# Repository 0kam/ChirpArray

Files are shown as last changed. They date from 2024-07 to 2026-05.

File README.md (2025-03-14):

# `ChirpArray`: a low-cost, easy-to-build microphone array for long-term ecoacoustic monitoring 

## Overview
`ChirpArray` is a microphone array for outdoor recording projects.  
It utilizes Sony's Spresense microcontroller as a processing module.
See https://doi.org/10.1111/2041-210X.14474 for more detail.

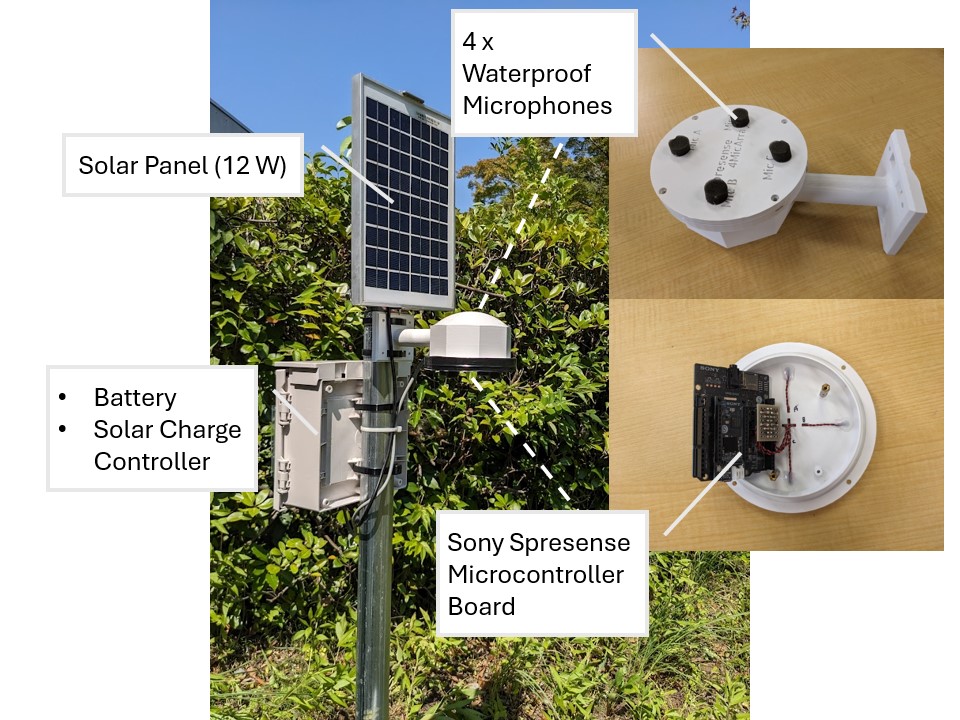
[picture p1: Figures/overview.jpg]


## Features
- **Up to 4ch recording:**  
    `ChirpArray` has 4 microphones to enable sound source localization.
- **Flexible recording setting and scheduling:**  
    Plenty of options for various research projects:
    * Sampling rate (16 kHz ~ 192 kHz)
    * Channels of recording (monaural, stereo, 4 channels)
    * Audio codec (WAV or MP3)
    * Recording schedule (see below) 
- **Low power consumption:**  
    `ChirpArray` can run with a 12 W solar power system due to Spresense's low power features.
- **Automated time correction using on-board GNSS**
- **Low cost:**  
    The whole system with solar power system costs about $200.
- **Easy to reproduce:**  
    All parts are available online.  
    No professional skills are required to assemble `ChirpArray`.

## Parts list
### `ChirpArray`  
| product name | product type | manufacture | price | quantity |
| --- | --- | --- | --- | --- |
| Spresense Main Board | Main processing board | SONY | ¥6000 | 1 |
| Spresense Extension Board | Extension board for microphone inputs | SONY | ¥4000 | 1 |
| CME-1538-100LB | Analogue microphone | CUI Devices | ¥500 | 4 |
| 2.2 kΩ carbon resister | general resister |  | Under ¥10 | 4 |
| Stripboard (36 mm x 24 mm) | general stripboard |  | Under ¥100 | 1 |
| pin header (2 x 8) | general pin header |  | Under ¥50 | 1 |
| micro SD Card (512GB) | general micro SD card |  | ¥10000 | 1 |

### *Optional:* Parts Example for Solar Powered Applications
| product name | product type | manufacture | price | quantity |
| --- | --- | --- | --- | --- |
| SY-M12W-12 | Solar Panel (12 W) | SANYOOO solar | ¥2500 | 1 |
| SA-BA10 | Solar Charge Controller | DENRYO | ¥4000 | 1 |
| WP7.2-12 | Battery (12 V, 7,2 Ah) | Kung Long Batteries Industrial | ¥3000 | 1 |

### *Optional* recommended off-the-shelf waterproof box
[Takachi BCAP151509G](https://www.takachi-el.co.jp/assets/attachments/images/BCAP151509G.pdf) (¥1,600)

## Hardware Assembling

### Water-proof enclosures
First, choose a case to house the Spresense. While we have published 3D models of cases that can be printed with a 3D printer, you can also use commercially available waterproof boxes for outdoor installations. If you opt for a commercially available case, select one with enough space to accommodate the Spresense Extension Board (at least 90mm x 90mm x 30mm). Commercially available cases tend to offer better waterproofing, so if you're installing the device near a pond or in a high-humidity environment, it might be better to go with a commercially available case.
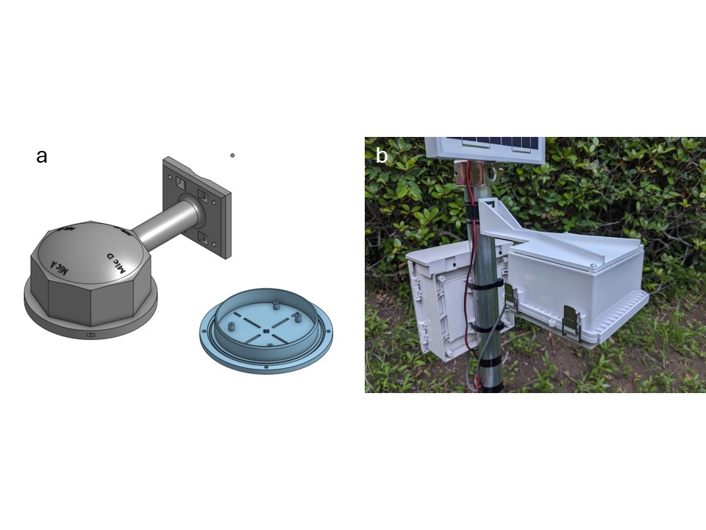
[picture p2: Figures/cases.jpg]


### Placing microphones
Next, arrange each microphone at equal intervals around the circumference of an 8cm diameter circle. If you are using a printable case, attach the microphones as shown in the picture below, and route the wires inside the case. Seal the wire entry points with adhesive. If you are using a commercially available case, drill holes in the case to attach the microphones directly. We also provide a 3D model for a microphone mounting plate, which you can print and use with any cases (in `3Dprintables/off_the_shelf_cases/MicrophoneAdaptor.stl`). To avoid rain damage, please install the microphones on the underside of the case.

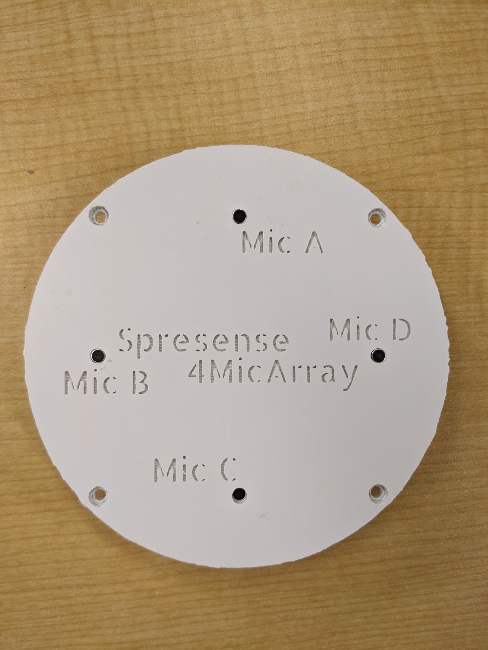
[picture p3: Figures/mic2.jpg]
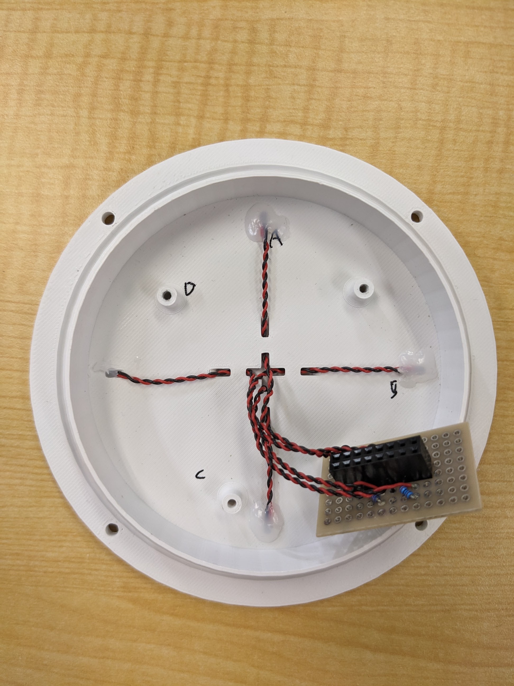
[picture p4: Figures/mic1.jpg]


### Wiring microphones
Finally, wire the microphones. I recommend reading [the official tutorial](https://developer.sony.com/spresense/tutorials-sample-projects/spresense-tutorials/using-multiple-microphone-inputs-with-spresense) and [the hardware documentation](https://developer.sony.com/spresense/development-guides/hw_docs_en.html#_how_to_use_microphones) as well.
1. Attatch Sony Spresense to the Spresense Extension Board  
    See [here](https://developer.sony.com/develop/spresense/docs/introduction_en.html#_how_to_attach_the_spresense_extension_board_and_the_spresense_main_board) for more details.
2. Wire the microphones and bias resisters.
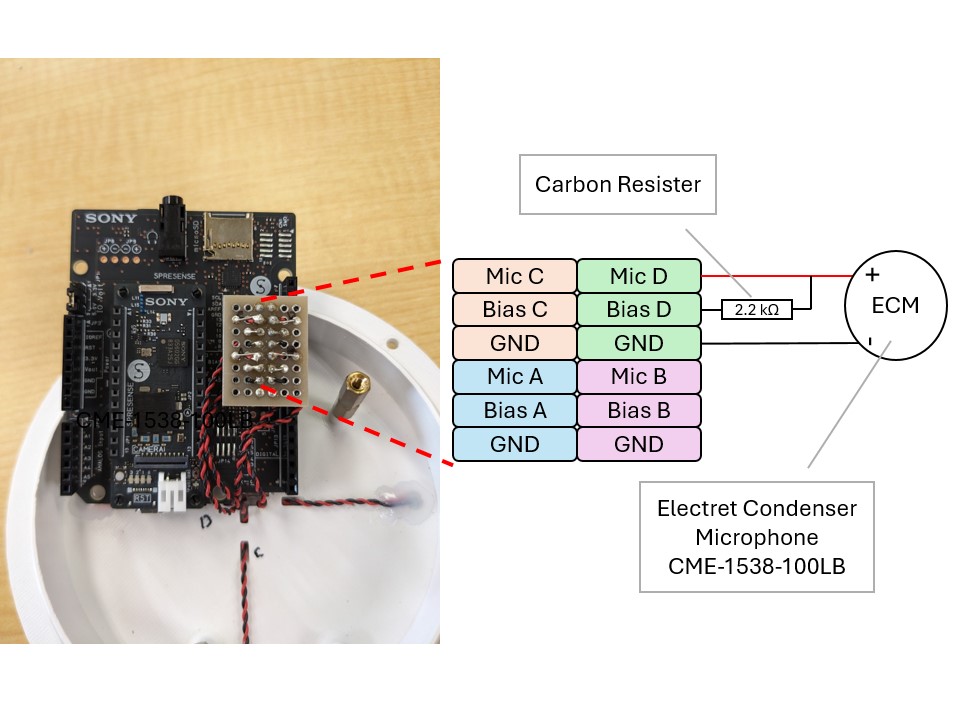
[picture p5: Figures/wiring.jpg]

The pin assignment of the Spresense Extension Board is shown as below. Follow the "Analogue" microphone placement and wire each microphone.  Make sure that each microphone is connected to the correct location.

>https://developer.sony.com/spresense/development-guides/images/HW_Mic_placement_E.png

### *3D models*
The 3D models were designed using Onshape and free to use and modify. See [the Onshape document](https://cad.onshape.com/documents/03e8f32e7241855707f43321/w/463fb24775ae6009ebde1d43/e/08f62e0ab2deafdc8f3bd898?renderMode=0&uiState=667e794788fb99170249fb00).

## Software Installation
1. Installing ArduinoIDE   
2. Setting up your Sony Spresense   

>For Step1. and 2., please refer to the [official tutorial](https://developer.sony.com/spresense/development-guides/arduino_set_up_en.html).

3. Setting recording options  
See [the Arduino Sketch](Arduino/timelapse_recorder/timelapse_recorder.ino) for more detail.    
You can set recording schedule, channels of recordings, sampling rate, and audio codec.

## How can I choose batteries and micro-SD cards?
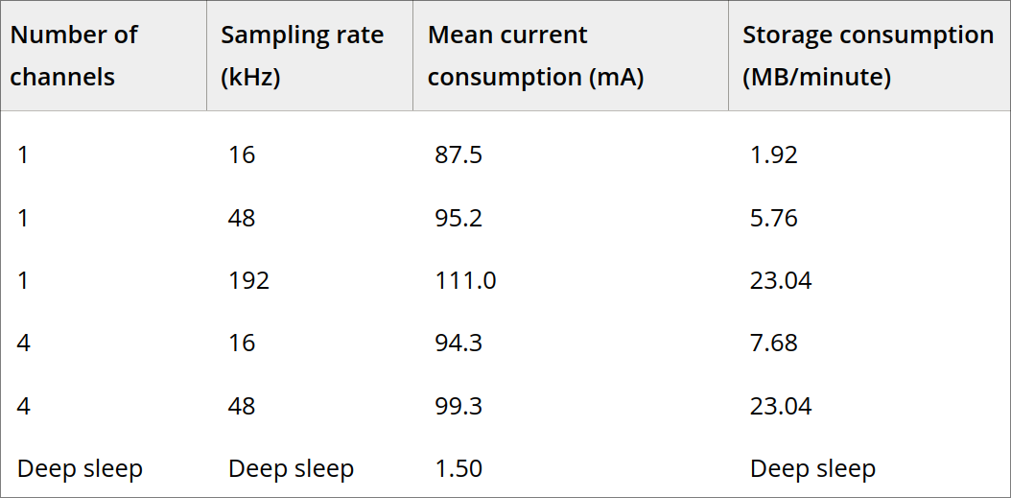
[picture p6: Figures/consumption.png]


## How to cite
 Okamoto, R., & Oguma, H. (2025). ChirpArray: A low-cost, easy-to-construct microphone array for long-term ecoacoustic monitoring. Methods in Ecology and Evolution, 16, 302–308. https://doi.org/10.1111/2041-210X.14474 

```
@article{https://doi.org/10.1111/2041-210X.14474,
author = {Okamoto, Ryotaro and Oguma, Hiroyuki},
title = {ChirpArray: A low-cost, easy-to-construct microphone array for long-term ecoacoustic monitoring},
journal = {Methods in Ecology and Evolution},
volume = {16},
number = {2},
pages = {302-308},
keywords = {automated recording unit, ecoacoustics, microphone array},
doi = {https://doi.org/10.1111/2041-210X.14474},
url = {https://besjournals.onlinelibrary.wiley.com/doi/abs/10.1111/2041-210X.14474},
eprint = {https://besjournals.onlinelibrary.wiley.com/doi/pdf/10.1111/2041-210X.14474},
abstract = {Abstract Advances in passive acoustic monitoring (PAM) have highlighted the importance of recording devices and audio recognition techniques in ecosystem monitoring. This study introduces ChirpArray, a cost-effective and easily assembled microphone array for long-term ecoacoustic monitoring of outdoor ecosystems. The ChirpArray system features a four-channel microphone array that estimates sound source directions, aids in identifying individual animals and provides a detailed behavioural analysis. Unlike previous microphone arrays, ChirpArray is low-cost, low-power and waterproof, making it ideal for extended-field monitoring. It is a fully open source and is constructed from readily available materials, ensuring broad accessibility for applications ranging from local citizen projects to large-scale landscape recordings. This study details the power, storage consumption and localization performance of ChirpArray. Current measurements show that a small solar-power set-up can continuously operate the system. Localization tests using loudspeakers have yielded promising results. ChirpArray is a compact, energy-efficient microphone array designed for long-term outdoor recording, offering considerable advantages in ecoacoustic monitoring. Its exceptionally low power consumption allows for efficient and flexible deployment, making it an ideal solution for extended-field monitoring and large-scale landscape recordings.},
year = {2025}
}
```

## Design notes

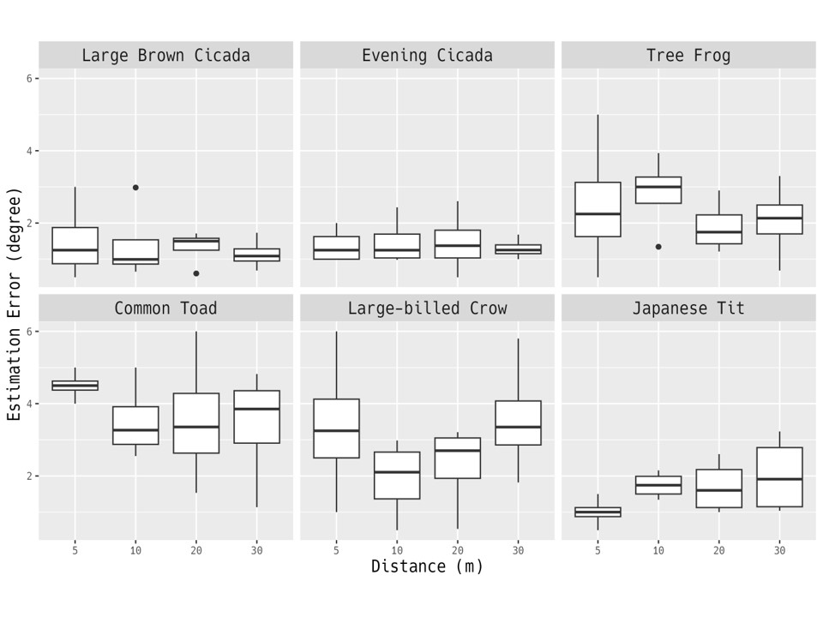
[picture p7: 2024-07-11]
Figures/azimuth_error.jpg

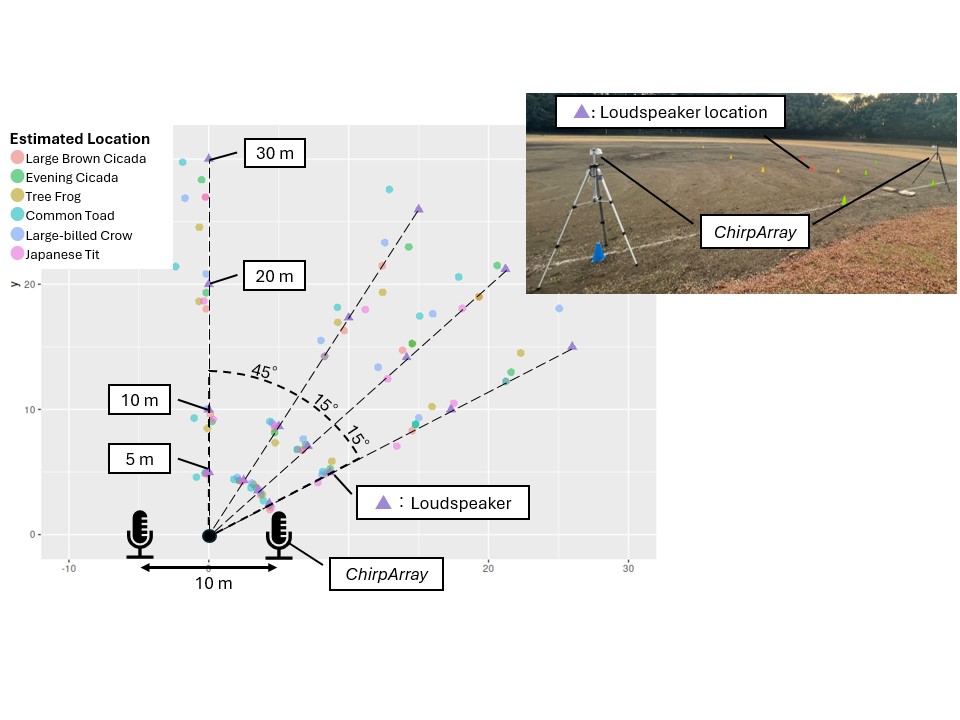
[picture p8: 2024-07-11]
Figures/localization.jpg

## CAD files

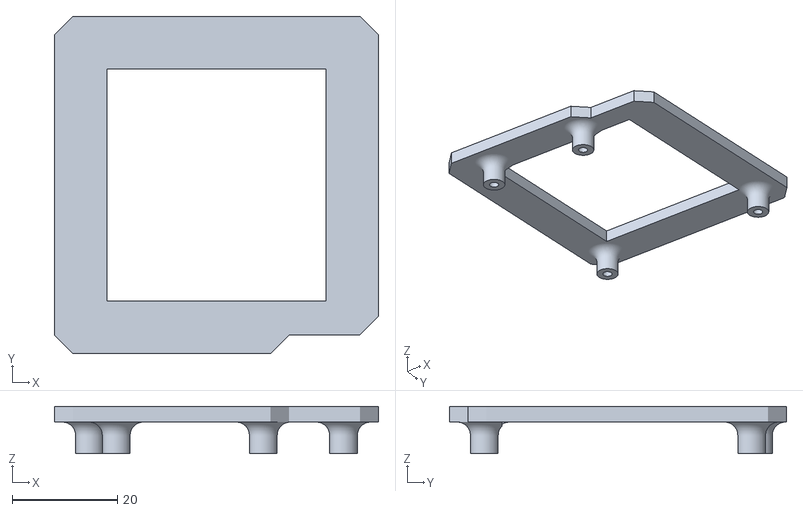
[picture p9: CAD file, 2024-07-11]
3Dprintables/off_the_shelf_cases/SprensenseExtensionBoardMount.stl
61.6 x 64.1 x 9.00

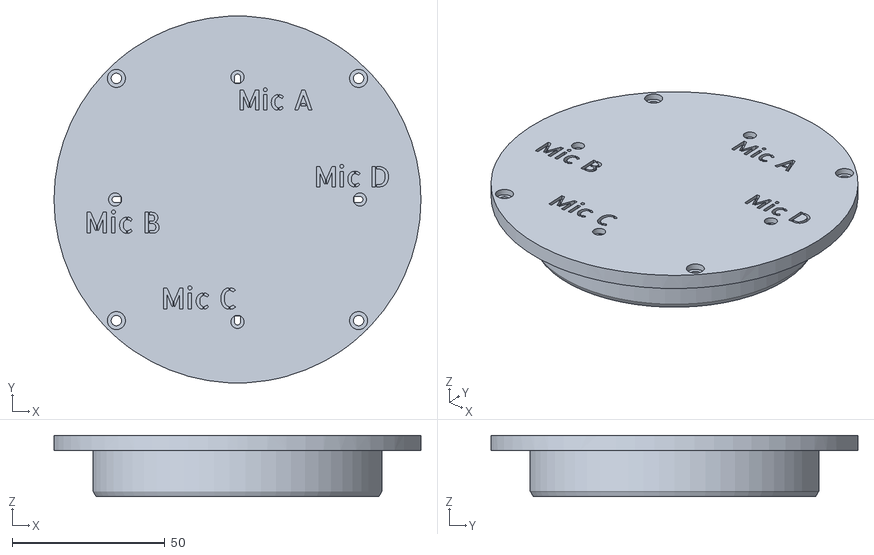
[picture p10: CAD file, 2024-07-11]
3Dprintables/printable_case/Printable case - MicrophonePlate.stl
120.0 x 120.0 x 20.0

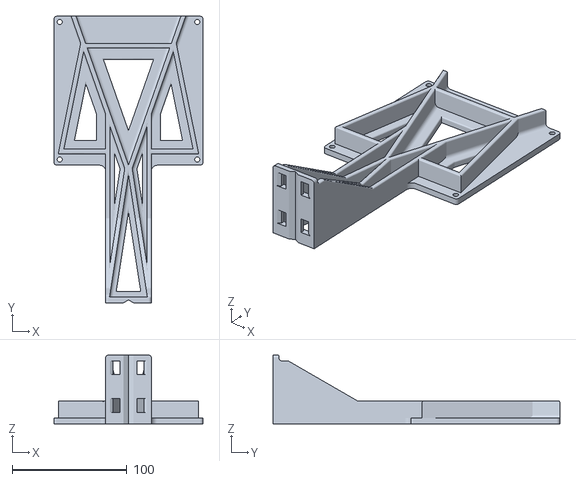
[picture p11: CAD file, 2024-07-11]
3Dprintables/off_the_shelf_cases/CaseMount_for_TakachiBox.stl
130.0 x 250.0 x 60.0

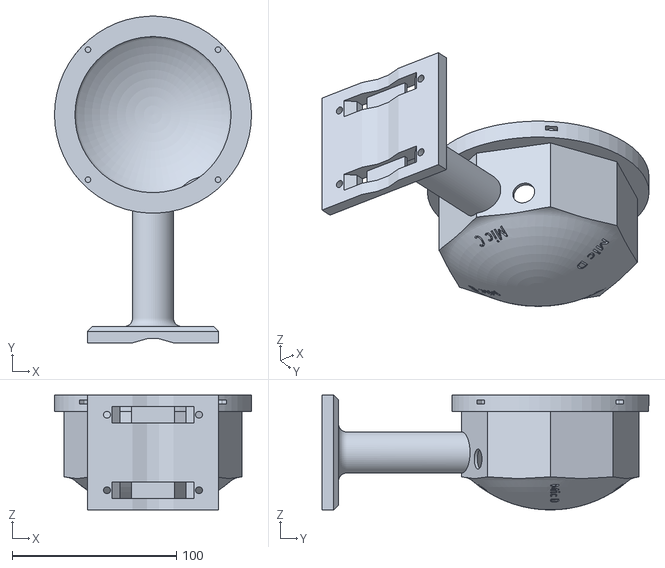
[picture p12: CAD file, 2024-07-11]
3Dprintables/printable_case/Printable case - TopCase.stl
120.0 x 199.0 x 70.0

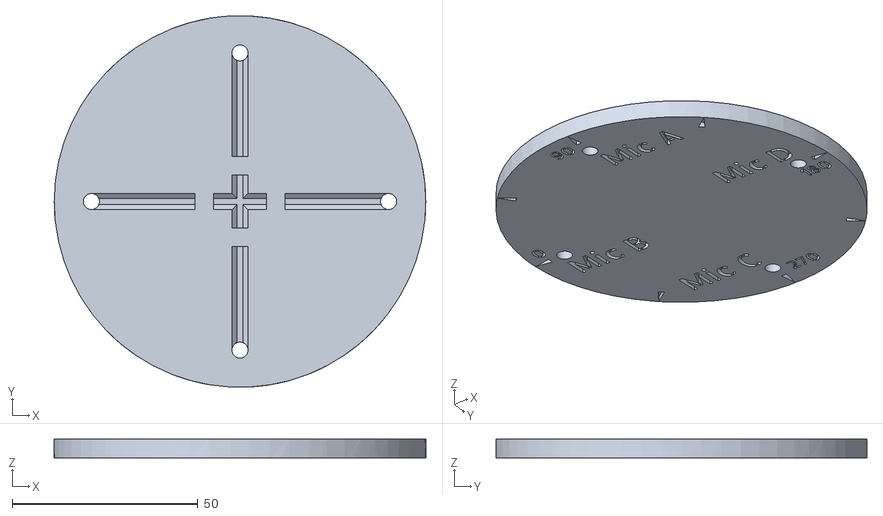
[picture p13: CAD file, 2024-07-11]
3Dprintables/off_the_shelf_cases/MicrophoneAdaptor.stl
100.0 x 99.9 x 5.00

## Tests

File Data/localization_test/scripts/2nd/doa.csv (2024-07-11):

condition | sound | mic | doa
0deg10m | aburazemi.wav | micL | 62.0
0deg10m | aburazemi.wav | micR | 117.0
0deg10m | higurashi.wav | micL | 60.99999999999999
0deg10m | higurashi.wav | micR | 118.00000000000001
0deg10m | karasu.wav | micL | 64.0
0deg10m | karasu.wav | micR | 117.0
0deg10m | shijukara.wav | micL | 60.99999999999999
0deg10m | shijukara.wav | micR | 117.0
0deg10m | hikigaeru.wav | micL | 67.0
0deg10m | hikigaeru.wav | micR | 123.0
0deg10m | amagaeru.wav | micL | 60.99999999999999
0deg10m | amagaeru.wav | micR | 121.00000000000001
0deg20m | aburazemi.wav | micL | 75.0
0deg20m | aburazemi.wav | micR | 106.0
0deg20m | higurashi.wav | micL | 76.00000000000001
0deg20m | higurashi.wav | micR | 105.0
0deg20m | karasu.wav | micL | 77.0
0deg20m | karasu.wav | micR | 104.00000000000001
0deg20m | shijukara.wav | micL | 76.00000000000001
0deg20m | shijukara.wav | micR | 106.0
0deg20m | hikigaeru.wav | micL | 83.0
0deg20m | hikigaeru.wav | micR | 108.99999999999999
0deg20m | amagaeru.wav | micL | 77.0
0deg20m | amagaeru.wav | micR | 107.0
0deg30m | aburazemi.wav | micL | 80.0
0deg30m | aburazemi.wav | micR | 101.0
0deg30m | higurashi.wav | micL | 81.0
0deg30m | higurashi.wav | micR | 101.0
0deg30m | karasu.wav | micL | 83.0
0deg30m | karasu.wav | micR | 104.00000000000001
0deg30m | shijukara.wav | micL | 80.0
0deg30m | shijukara.wav | micR | 101.0
0deg30m | hikigaeru.wav | micL | 84.0
0deg30m | hikigaeru.wav | micR | 103.00000000000001
0deg30m | amagaeru.wav | micL | 80.0
0deg30m | amagaeru.wav | micR | 103.00000000000001
0deg5m | aburazemi.wav | micL | 45.0
0deg5m | aburazemi.wav | micR | 136.00000000000003
0deg5m | higurashi.wav | micL | 46.0
0deg5m | higurashi.wav | micR | 137.0
0deg5m | karasu.wav | micL | 46.0
0deg5m | karasu.wav | micR | 136.00000000000003
0deg5m | shijukara.wav | micL | 45.0
0deg5m | shijukara.wav | micR | 137.0
0deg5m | hikigaeru.wav | micL | 48.0
0deg5m | hikigaeru.wav | micR | 142.0
0deg5m | amagaeru.wav | micL | 45.0
0deg5m | amagaeru.wav | micR | 136.00000000000003
30deg10m | aburazemi.wav | micL | 41.0
30deg10m | aburazemi.wav | micR | 92.0
30deg10m | higurashi.wav | micL | 40.0
30deg10m | higurashi.wav | micR | 92.0
30deg10m | karasu.wav | micL | 43.0
30deg10m | karasu.wav | micR | 93.00000000000001
30deg10m | shijukara.wav | micL | 42.0
30deg10m | shijukara.wav | micR | 92.0
30deg10m | hikigaeru.wav | micL | 44.0
30deg10m | hikigaeru.wav | micR | 94.0
30deg10m | amagaeru.wav | micL | 37.0
30deg10m | amagaeru.wav | micR | 92.0
30deg20m | aburazemi.wav | micL | 48.0
30deg20m | aburazemi.wav | micR | 74.0
30deg20m | higurashi.wav | micL | 47.0
30deg20m | higurashi.wav | micR | 77.0
30deg20m | karasu.wav | micL | 50.0
30deg20m | karasu.wav | micR | 79.0
30deg20m | shijukara.wav | micL | 47.0
30deg20m | shijukara.wav | micR | 77.99999999999999
30deg20m | hikigaeru.wav | micL | 52.00000000000001
30deg20m | hikigaeru.wav | micR | 77.99999999999999
30deg20m | amagaeru.wav | micL | 50.0
30deg20m | amagaeru.wav | micR | 76.00000000000001
30deg30m | aburazemi.wav | micL | 51.0
30deg30m | aburazemi.wav | micR | 71.0
30deg30m | higurashi.wav | micL | 50.0
30deg30m | higurashi.wav | micR | 68.00000000000001
30deg30m | karasu.wav | micL | 53.0
30deg30m | karasu.wav | micR | 72.0
30deg30m | shijukara.wav | micL | 48.99999999999999
30deg30m | shijukara.wav | micR | 71.0
30deg30m | hikigaeru.wav | micL | 57.00000000000001
30deg30m | hikigaeru.wav | micR | 74.0
30deg30m | amagaeru.wav | micL | 48.0
30deg30m | amagaeru.wav | micR | 69.0
30deg5m | aburazemi.wav | micL | 30.0
30deg5m | aburazemi.wav | micR | 121.99999999999999
30deg5m | higurashi.wav | micL | 31.0
30deg5m | higurashi.wav | micR | 123.0
30deg5m | karasu.wav | micL | 33.0
30deg5m | karasu.wav | micR | 123.0
30deg5m | shijukara.wav | micL | 30.0
30deg5m | shijukara.wav | micR | 121.99999999999999
30deg5m | hikigaeru.wav | micL | 33.0
30deg5m | hikigaeru.wav | micR | 125.99999999999999
30deg5m | amagaeru.wav | micL | 31.0
30deg5m | amagaeru.wav | micR | 123.0
45deg10m | aburazemi.wav | micL | 31.0
45deg10m | aburazemi.wav | micR | 79.0
45deg10m | higurashi.wav | micL | 31.0
45deg10m | higurashi.wav | micR | 75.0
45deg10m | karasu.wav | micL | 33.0
45deg10m | karasu.wav | micR | 77.0
45deg10m | shijukara.wav | micL | 30.0
45deg10m | shijukara.wav | micR | 76.00000000000001
45deg10m | hikigaeru.wav | micL | 31.0
45deg10m | hikigaeru.wav | micR | 79.0
45deg10m | amagaeru.wav | micL | 30.0
45deg10m | amagaeru.wav | micR | 76.00000000000001
45deg20m | aburazemi.wav | micL | 38.00000000000001
45deg20m | aburazemi.wav | micR | 59.00000000000001
45deg20m | higurashi.wav | micL | 38.99999999999999
45deg20m | higurashi.wav | micR | 58.00000000000001
45deg20m | karasu.wav | micL | 38.00000000000001
45deg20m | karasu.wav | micR | 62.0
45deg20m | shijukara.wav | micL | 35.0
45deg20m | shijukara.wav | micR | 58.00000000000001
45deg20m | hikigaeru.wav | micL | 41.0
45deg20m | hikigaeru.wav | micR | 60.99999999999999
45deg20m | amagaeru.wav | micL | 38.00000000000001
45deg20m | amagaeru.wav | micR | 58.00000000000001
45deg30m | aburazemi.wav | micL | 38.99999999999999
45deg30m | aburazemi.wav | micR | 53.0
45deg30m | higurashi.wav | micL | 40.0
45deg30m | higurashi.wav | micR | 54.0
45deg30m | karasu.wav | micL | 40.0
45deg30m | karasu.wav | micR | 58.00000000000001
45deg30m | shijukara.wav | micL | 38.00000000000001
45deg30m | shijukara.wav | micR | 54.0
45deg30m | hikigaeru.wav | micL | 42.0
45deg30m | hikigaeru.wav | micR | 58.00000000000001
45deg30m | amagaeru.wav | micL | 38.99999999999999
45deg30m | amagaeru.wav | micR | 53.0
45deg5m | aburazemi.wav | micL | 20.0
45deg5m | aburazemi.wav | micR | 112.0
45deg5m | higurashi.wav | micL | 24.0
45deg5m | higurashi.wav | micR | 113.0
45deg5m | karasu.wav | micL | 27.0
45deg5m | karasu.wav | micR | 114.99999999999999
45deg5m | shijukara.wav | micL | 23.0
45deg5m | shijukara.wav | micR | 112.0
45deg5m | hikigaeru.wav | micL | 25.0
45deg5m | hikigaeru.wav | micR | 118.00000000000001
45deg5m | amagaeru.wav | micL | 26.000000000000004
45deg5m | amagaeru.wav | micR | 114.00000000000001
60deg10m | aburazemi.wav | micL | 20.0
60deg10m | aburazemi.wav | micR | 55.00000000000001
60deg10m | higurashi.wav | micL | 21.0
60deg10m | higurashi.wav | micR | 55.00000000000001
60deg10m | karasu.wav | micL | 20.0
60deg10m | karasu.wav | micR | 57.00000000000001
60deg10m | shijukara.wav | micL | 18.0
60deg10m | shijukara.wav | micR | 56.0
60deg10m | hikigaeru.wav | micL | 21.0
60deg10m | hikigaeru.wav | micR | 58.00000000000001
60deg10m | amagaeru.wav | micL | 23.0
60deg10m | amagaeru.wav | micR | 57.00000000000001
60deg20m | aburazemi.wav | micL | 23.0
60deg20m | aburazemi.wav | micR | 41.0
60deg20m | higurashi.wav | micL | 24.0
60deg20m | higurashi.wav | micR | 42.0
60deg20m | karasu.wav | micL | 25.0
60deg20m | karasu.wav | micR | 43.0
60deg20m | shijukara.wav | micL | 21.0
60deg20m | shijukara.wav | micR | 40.0
60deg20m | hikigaeru.wav | micL | 24.0
60deg20m | hikigaeru.wav | micR | 42.0
60deg20m | amagaeru.wav | micL | 26.000000000000004
60deg20m | amagaeru.wav | micR | 43.0
60deg30m | aburazemi.wav | micL | 25.0
60deg30m | aburazemi.wav | micR | 37.0
60deg30m | higurashi.wav | micL | 26.000000000000004
60deg30m | higurashi.wav | micR | 38.99999999999999
60deg30m | karasu.wav | micL | 31.0
60deg30m | karasu.wav | micR | 42.0
60deg30m | shijukara.wav | micL | 25.0
60deg30m | shijukara.wav | micR | 40.0
60deg30m | hikigaeru.wav | micL | 25.0
60deg30m | hikigaeru.wav | micR | 37.0
60deg30m | amagaeru.wav | micL | 28.0
60deg30m | amagaeru.wav | micR | 40.0
60deg5m | aburazemi.wav | micL | 12.0
60deg5m | aburazemi.wav | micR | 108.0
60deg5m | higurashi.wav | micL | 14.0
60deg5m | higurashi.wav | micR | 106.0
60deg5m | karasu.wav | micL | 21.0
60deg5m | karasu.wav | micR | 111.0
60deg5m | shijukara.wav | micL | 13.000000000000002
60deg5m | shijukara.wav | micR | 104.00000000000001
60deg5m | hikigaeru.wav | micL | 17.000000000000004
60deg5m | hikigaeru.wav | micR | 112.0
60deg5m | amagaeru.wav | micL | 20.0
60deg5m | amagaeru.wav | micR | 110.00000000000001

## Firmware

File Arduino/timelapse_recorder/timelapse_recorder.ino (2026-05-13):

/*
---------------------
Name: timelapse_recorder.ino
Author: Ryotaro Okamoto
Started: 2023/1/30
Last Modified: 2025/07/15
Purpose: To perform time-lapse audio recordings using Sony Spresense
Reference: https://doi.org/10.1111/2041-210X.14474
---------------------
Description:
This script is for making time-lapse audio recoder with Sony Spresense.
You can record a given length of audio and write it to .wav or .mp3 file.
This script performs an interval recording with a given schedule (the starting time, ending time, and interval).

The overview of the recording process is:
1. Recieving GNSS signals and set RTC time (Only at the first boot).
2. Recording and saving an audio.
3. Calculate the next booting time.
4. Going to deep sleep.

You must install DSP files in your SD card before starting. Follow the instruction below.
https://developer.sony.com/spresense/development-guides/arduino_tutorials_en.html#_install_dsp_files

Also you can learn how to attach a microphone to your Spresense with the document below.
https://developer.sony.com/spresense/development-guides/hw_docs_en.html#_how_to_use_microphones

Please make sure that the memory size is set to be 1024 kb (Tools -> Memory in ArduinoIDE, especially in HiRes recording)

Sometime the recording preocess fails for some reason (e.g., audio library error, file writing wrror).
This script utilizes the Watchdog function of Spresense to avoid the whole process freezing after such errors.
The Watchdog monitors the recording loop and if something wrong happened (e.g., file writing error), it will kill the process and reset the hardware.
*/

// Loading libraries
#include <GNSS.h>
#include <LowPower.h>
#include <RTC.h>

// Defining the schedule structure
typedef struct { 
 int start_h;
 int end_h;
 int m[100];
} schedule;

#include <SDHCI.h>
#include <Audio.h>
#include <Watchdog.h>
#define BAUDRATE 115200
#define MY_TIMEZONE_IN_SECONDS (9 * 60 * 60) // 9 * 60 * 60 means JST. Modify if required since the GNSS time is UTC.

enum operation_mode_t {
  MODE_TIMELAPSE,
  MODE_CONTINUOUS
};

/* Operation mode
-----------------------------------------------------------------------------------------------*/
static const operation_mode_t operation_mode = MODE_TIMELAPSE;
static const int continuous_start_index = 1;
/*---------------------------------------------------------------------------------------------*/

/* Time-lapse Parameters
-----------------------------------------------------------------------------------------------*/
schedule s = {17,7, {0,10, 20, 30, 40, 50}}; // {start time (O'clock), end time (O'clock), {start time in every hour}}
// Above schedule means that the recording starts at 0min, 5min, 10min, 15min in every hour from 1:00 to 24:00.
//If you specify s = {17,7,{0,20,40}}, The recording will be start at 17:00 and stop at 7:00 (7:20 and 7:40 will not be created).
/*---------------------------------------------------------------------------------------------*/

/* Audio Parameters
-----------------------------------------------------------------------------------------------*/
/* The audio codec. AS_CODECTYPE_MP3 or AS_CODECTYPE_WAV */
static const int32_t codec =  AS_CODECTYPE_WAV;

/*---------- 
The recording time in sec. 
Note that finishing recording requires about 10 seconds.
Long recording time (10 min >) may cause file writing error.
If you want to record a long audio, you should divide it into several short recordings.

Example: Recording 20 min audio in every O'clock
schedule s = {1, 24, {0, 5, 10, 15}}; // Start recording at 0min, 5min, 10min, 15min in every hour
static const int32_t recording_time = 290; // 290 sec = 4min 50sec (10 sec for finishing recording)
*/
static const int32_t recording_time = 300;

/*----------
The gain of the microphone.
The range is 0 to 21 [dB] for analog microphones and -78.5 to 0 [dB] for digital microphones.
For an analog microphone, specify an integer value multiplied by 10 for input_gain, for example, 100 when setting 10 [dB].
For a digital microphone, specify an integer value multiplied by 100 for input_gain, for example -5 when setting -0.05 [dB].
*/
static const int32_t gain = 100; // Max gain is 210, that means 21dB

/* ----------
Using digital mic? 
ChirpArray uses analog microphone, so set false.
*/
static const bool is_digital = false;

/*----------
Mono or Stereo? 
AS_CHANNEL_STEREO, AS_CHANNEL_STEREO, or AS_CHANNEL_4CH 
*/
static const int32_t channel = AS_CHANNEL_4CH;

/*---------- 
The sumpling rate. MP3 supports 48kHz ( AS_SAMPLINGRATE_48000 ) 
WAV supports 16000, 48000, 192000.
Note that 192 kHz recording is not available in 4CH recording due to the writing speed to the SD card.
*/
static const int32_t sr = AS_SAMPLINGRATE_16000;

/* ----------
The output directory to save audio files */
String out_dir = "AUDIO";

/*---------------------------------------------------------------------------------------------*/
/* Parameters for WAV recording
-----------------------------------------------------------------------------------------------*/
static const uint8_t  recoding_bit_length = 16; // Bitrate of wav recording. 16 or 24
/*---------------------------------------------------------------------------------------------*/


/* For timelapse operation
-----------------------------------------------------------------------------------------------*/
// Define when to start recording
static const int recording_start_second = 0; // start recording at 0 sec of each minutes
// Wating time between boot and recording
static const int boot_to_record_delay = 15; // boot 10 sec earlier than the recording time

const char* boot_cause_strings[] = {
  "Power On Reset with Power Supplied",
  "System WDT expired or Self Reboot",
  "Chip WDT expired",
  "WKUPL signal detected in deep sleep",
  "WKUPS signal detected in deep sleep",
  "RTC Alarm expired in deep sleep",
  "USB Connected in deep sleep",
  "Others in deep sleep",
  "SCU Interrupt detected in cold sleep",
  "RTC Alarm0 expired in cold sleep",
  "RTC Alarm1 expired in cold sleep",
  "RTC Alarm2 expired in cold sleep",
  "RTC Alarm Error occurred in cold sleep",
  "Unknown(13)",
  "Unknown(14)",
  "Unknown(15)",
  "GPIO detected in cold sleep",
  "GPIO detected in cold sleep",
  "GPIO detected in cold sleep",
  "GPIO detected in cold sleep",
  "GPIO detected in cold sleep",
  "GPIO detected in cold sleep",
  "GPIO detected in cold sleep",
  "GPIO detected in cold sleep",
  "GPIO detected in cold sleep",
  "GPIO detected in cold sleep",
  "GPIO detected in cold sleep",
  "GPIO detected in cold sleep",
  "SEN_INT signal detected in cold sleep",
  "PMIC signal detected in cold sleep",
  "USB Disconnected in cold sleep",
  "USB Connected in cold sleep",
  "Power On Reset",
};

void printBootCause(bootcause_e bc)
{
  Serial.println("--------------------------------------------------");
  Serial.print("Boot Cause: ");
  Serial.print(boot_cause_strings[bc]);
  if ((COLD_GPIO_IRQ36 <= bc) && (bc <= COLD_GPIO_IRQ47)) {
    // Wakeup by GPIO
    int pin = LowPower.getWakeupPin(bc);
    Serial.print(" <- pin ");
    Serial.print(pin);
  }
  Serial.println();
  Serial.println("--------------------------------------------------");
}

SpGnss Gnss;
int continuous_index = continuous_start_index;

String printClock(RtcTime &rtc)
{
  char buf [13];
  sprintf(buf,
          "%04d%02d%02d_%02d%02d",
          rtc.year(), rtc.month(), rtc.day(),
          rtc.hour(), rtc.minute()
        );
  String str = String(buf);
  return str;
}

String printSequenceNumber(int index)
{
  char buf[13];
  sprintf(buf, "%06d", index);
  return String(buf);
}

void setRTC()
{
  // Initialize RTC at first
  RTC.begin();

  // Initialize and start GNSS library
  int ret;
  ret = Gnss.begin();
  assert(ret == 0);
  
  Gnss.select(GPS); // GPS
  Gnss.select(QZ_L1CA); // QZSS  
  Gnss.select(QZ_L1S);

  ret = Gnss.start();
  assert(ret == 0);

    // Wait for GNSS data
  int led_state = 0;
  while (true)
  {
    if (Gnss.waitUpdate()) {
      SpNavData  NavData;
  
      // Get the UTC time
      Gnss.getNavData(&NavData);
      SpGnssTime *time = &NavData.time;
  
      // Check if the acquired UTC time is accurate
      Serial.println(time->year);
      if (time->year > 2000 && time->year < 2100) {
        RtcTime now = RTC.getTime();
        // Convert SpGnssTime to RtcTime
        RtcTime gps(time->year, time->month, time->day,
                    time->hour, time->minute, time->sec, time->usec * 1000);
        // Set the time difference
        gps += MY_TIMEZONE_IN_SECONDS;
        int diff = now - gps;
        if (abs(diff) >= 1) {
          RTC.setTime(gps);
        }
        if (Gnss.stop() != 0)                
        {
          Serial.println("Gnss stop error!!");
        }
        else if (Gnss.end() != 0)            
        {
          Serial.println("Gnss end error!!");
        }
        ledOff(LED0);
        break;        
      }      
    }
    Serial.println("Waiting for GNSS signals...");
    if (led_state == 0)
    {
      ledOn(LED0);
      led_state = 1;
    }
    else
    {
      ledOff(LED0);
      led_state = 0;
    }
  }
}

void setLowPower()
{
  bootcause_e bc = LowPower.bootCause();
  if ((bc == POR_SUPPLY) || (bc == POR_NORMAL)) {
    Serial.println("ChirpArray starting!");
  } else {
    Serial.println("wakeup from deep sleep");
  }
  // Print the boot cause
  printBootCause(bc);
}

void findMinute(schedule s, int *next_minute, int *next_hour, int *next_date, RtcTime &rtc)
{
  bool find_m = false;
  int i;
  int m_len = sizeof(s.m) / sizeof(int);
  
  // Find a minute later than current time
  for (i = 0; i < m_len; i++)
  {
    if (s.m[i] > rtc.minute()){
      *next_minute = s.m[i];
      *next_hour = rtc.hour();
      *next_date = rtc.day();  // No date change since it's within the same hour
      find_m = true;
      break;
    }
  }
  
  // If no minute found later than current time, use the first minute of next hour
  if (!find_m)
  {
    *next_minute = s.m[0];
    *next_hour = rtc.hour() + 1;
    *next_date = rtc.day();
    
    // Handle case when hour exceeds 24
    if (*next_hour >= 24)
    {
      *next_hour = 0;
      *next_date = rtc.day() + 1;
    }
  }
}
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

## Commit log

2024-07-11 Added scripts
    [1ch192khz.csv, 4ch16khz.csv, doa.csv, doa_seg.csv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]
2024-10-18 Deleted unnecessary files
    [doa.csv, doa_seg.csv, doas.csv]
